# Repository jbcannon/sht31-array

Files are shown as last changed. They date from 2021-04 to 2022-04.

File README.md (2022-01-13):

# Overview

We have developed an open-platform temperature-humidity array for use in applications in forest and fire ecology. The following instructions provide step-by-step instructions for assembling the arrays and dataloggers. We also include software development and installation, and provide files to fabricate 3d-printed radiation shields, enclosures, and files necessary for manufacturing printed circuit boards for multiplexing.

 <p><p>Each section begins with materials required for assembly. Please read all instructions before begining to ensure all necessary materials are available. The material presented below details the construction of sensor and data loggers used in Cannon et al. (in prep). See manuscript for complete details on theory and applications.

* Complete assembly of [Particle Boron dataloggers](#data-logger-assembly-particle-boron-with-multiplexer) (1x)
* Fabricate [3d printed radiation shields](#3d-printed-radiation-shields) (8x shields)
* Fabricate [temperature and humidity sensor arrays](#SHT31-D-Sensor-arrays) (8x sensors)
* [Setting up Particle Boron-based dataloggers](#setup-and-test-boron-dataloggers)
  * Testing Particle Boron
  * Programing Particle Boron
  * Setting up cellular cloud data upload
 
<figure>
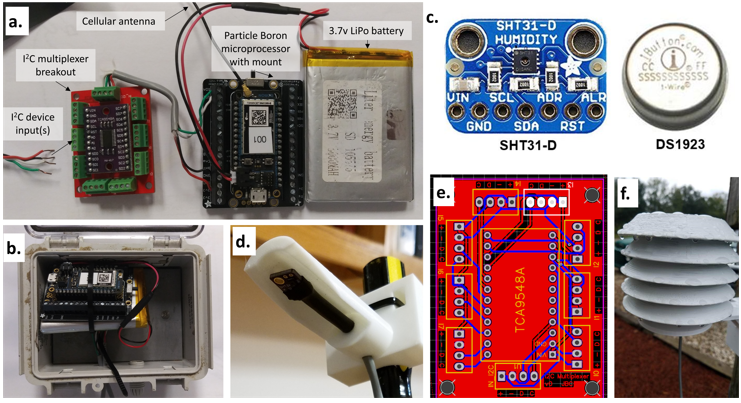
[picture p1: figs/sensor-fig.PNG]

<figcaption align = "center"><font size = -2>Figure 1. (a-f) Development of environmental monitoring using open-source platforms. (a) Datalogging assembly based on Particle Boron microprocessor on a screw terminal mount powered by a 3.7V 5000 mAH LiPo battery. Custom printed circuit board (PCB, red) includes I<sup>2</sup>C multiplexer chip allowing up to eight identically addressed sensors. (b) Datalogging assembly installed in weather resistant enclosure. (c) Comparison of Adafruit SHT31-D temperature and humidity sensor (left) and iButton Hygrochron (DS1932, right). (d) Minimalist radiation shield mount with installed SHT31-D sensor. (e) Custom PCB to use I<sup>2</sup>C multiplexer with 4-pin screw terminals. (f) 5-fin radiation shield 3D printed with PETG.<font></figcaption>
</figure>

 # Data logger Assembly (Particle Boron with multiplexer)
 
 Our system uses Particle Boron microcontrollers which have cellular network capabilities for remote data upload,  comprehensive documentation, and support numerous analog and digital devices using I<sup>2</sup>C or SPI. Our system uses multiple identically addressed SHT-31 sensors, which requires a multiplexer to allow reading of multiple sensors, thus we have created a custom printed circuit board that needs to be ordered or made.
 
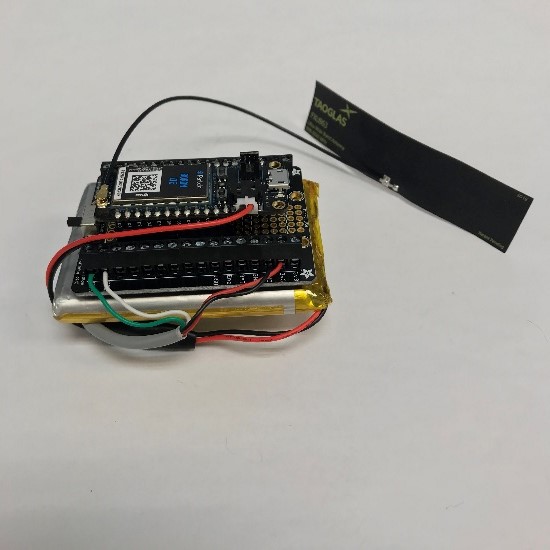
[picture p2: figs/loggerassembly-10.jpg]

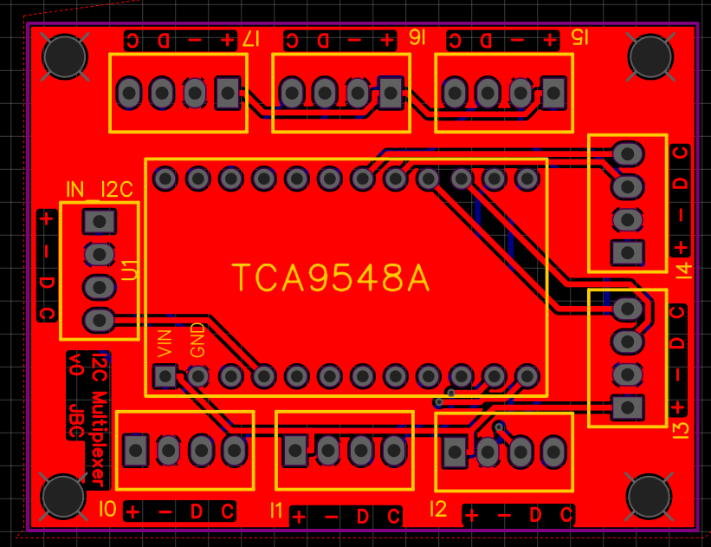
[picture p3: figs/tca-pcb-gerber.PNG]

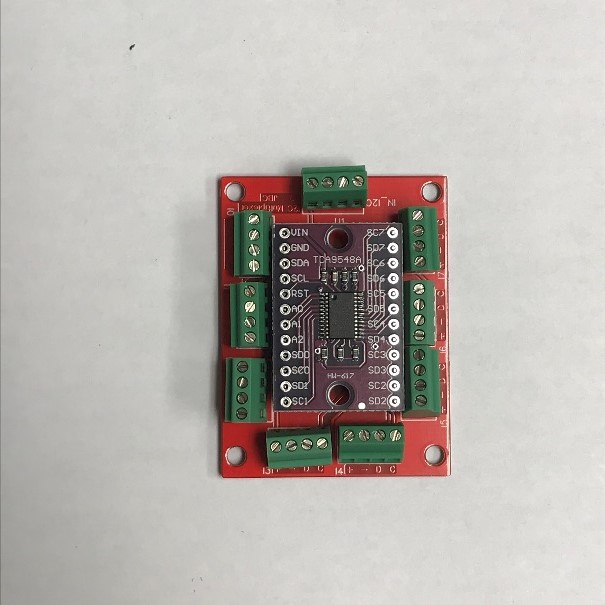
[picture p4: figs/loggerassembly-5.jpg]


 Follow the link to find complete instructions to <a href=pages/logger-assembly.md>assemble Particle Boron datalogger and multiplexer</a>

 # SHT31-D Sensor arrays

The SHT-31D sensor is an accurate temperature and humidity sensor with an accuracy of ±0.3°C and ±2% relative humidity. The sensor uses I<sup>2</sup>C connections and is therefore compatible with a wide variety of other I<sup>2</sup>C digital sensors, which allows for building more complex micro-meteorological stations.

 Follow the link to find complete instructions to <a href=pages/SHT-assembly.md>building SHT-31 sensor arrays</a>
 
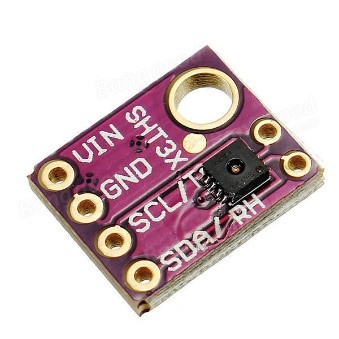
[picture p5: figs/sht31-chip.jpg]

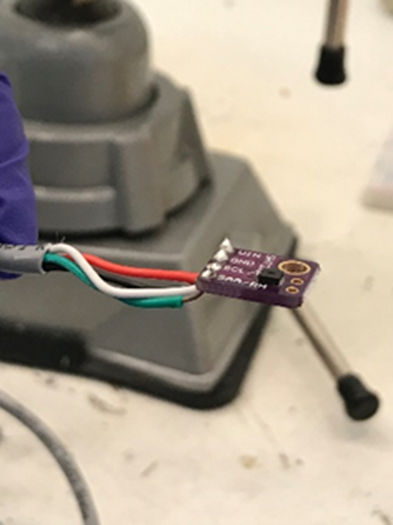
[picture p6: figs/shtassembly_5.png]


# 3D Printed radiation shields

To house the SHT31-D sensors, we provide plans and printing instructions for two radiation shield types, which include a minimalist radiation shield and a multi-fin radiation shield. 

Follow the link to find 3D models, photos, and printer settings for <a href=pages/3dprint.md>printing the radiation sheilds</a> on a PRUSA MK3 printer, or similar printer.

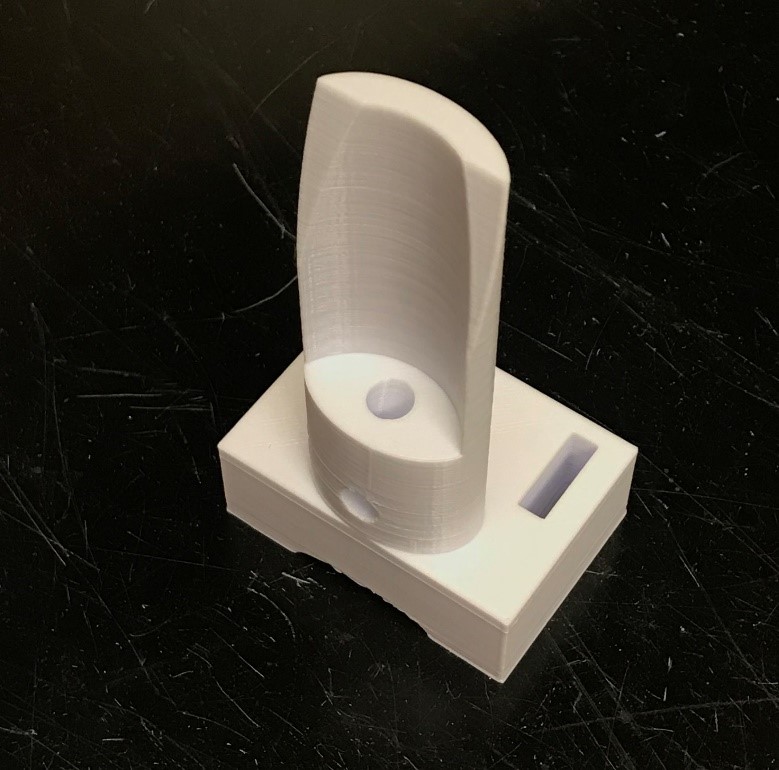
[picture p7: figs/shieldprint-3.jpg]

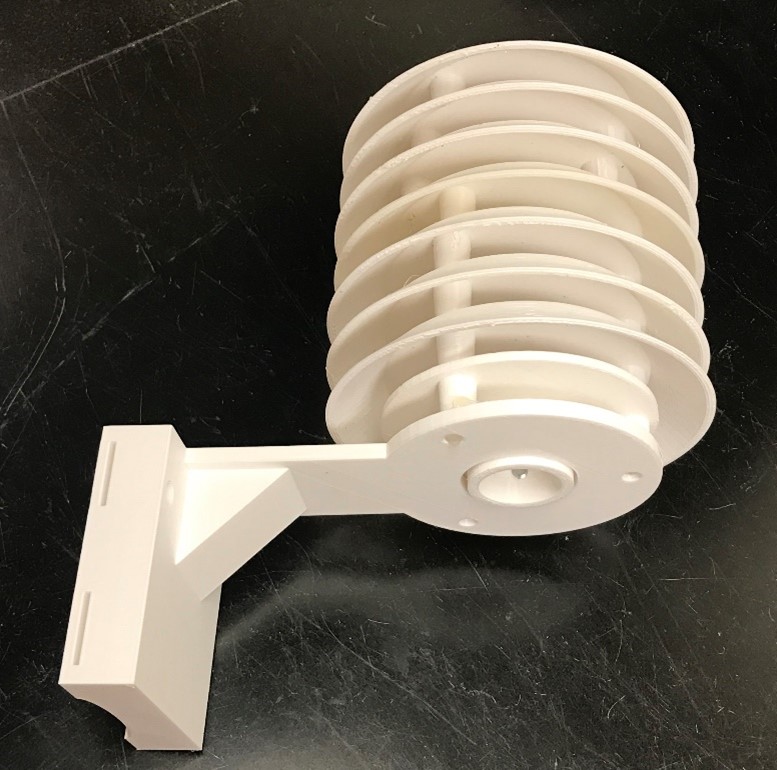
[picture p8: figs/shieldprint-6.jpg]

# Setup and test Boron dataloggers

Particle Boron offers a platform for interfacing with I<sup>2</sup>C sensors and connects to the web via cellular networks. 

Follow the link to find complete instructions to <a href=pages/boron-setup.md>activate and test Boron dataloggers<a/> with the SHT-31 sensors. The link includes instructions to activate through the Particle app for Android and iOS, testing upload apps and measurements, setting up cloud integration with Google Sheets, and deployment.

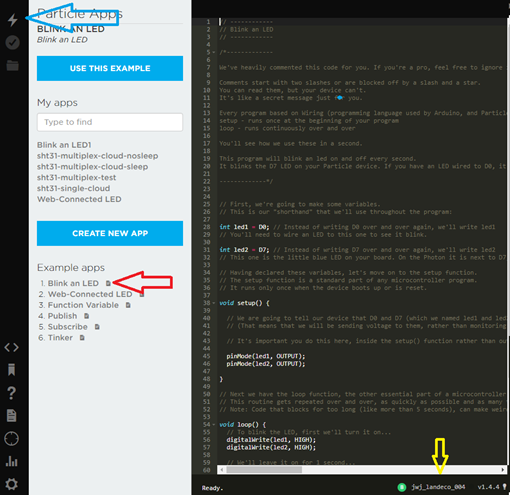
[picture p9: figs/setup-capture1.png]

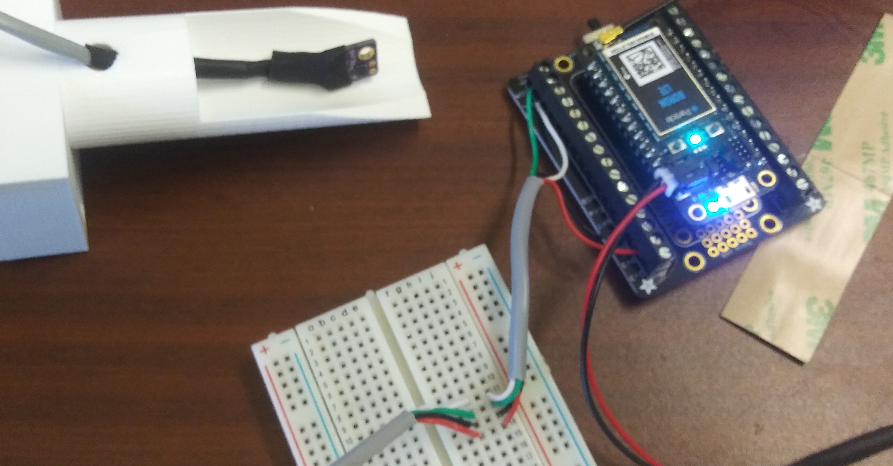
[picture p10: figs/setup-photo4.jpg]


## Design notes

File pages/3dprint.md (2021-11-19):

# SHT31-D 3D printed radiation shield

Our system uses a simple minimalist design for a 3d printed radiation shield. We provide plans and print settings for a minimalist radiation shield as well as a multi-fin radiation shield found on Thingiverse.  The following includes 3D model STL files used for housing SHT31-D sensors during field deployment, screenshots of two types of radiation shield models, 3D printer settings (for a Prusa I3 MK3S+ in PrusaSlicer software), and photographs of completed radiation shields.

## Tools & Materials
* PRUSA I3 MK3S+ 3D printer, or similar
* PrusaSlicer Software
* PETG filament, we recommend white
* Hot glue gun and glue cartridges or Cyanocoacrylate (CA) glue ("Super glue")

## Minimalist radiation shield

You can obtain a 3D model of the minimalist shield by downloading [minimalist-shield.stl](../files/minimalist-shield.stl).

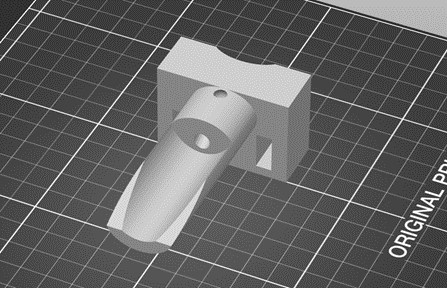
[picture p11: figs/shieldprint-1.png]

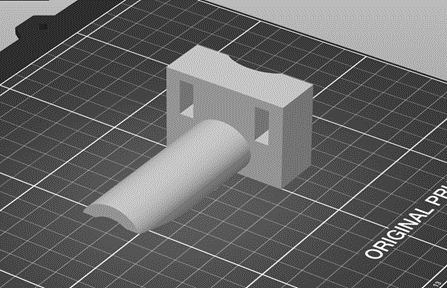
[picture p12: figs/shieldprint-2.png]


Using PRUSA Slicer, or similar software, we recommend the following print settings

| Printer setting | Recommended setting |
|----|---|
|Filament | Generic PETG |
| Nozzle temperature | 235°C |
| Bed temperature | 90°C |
| Layer Height | 0.2 mm (for all) |
| Infill | 25% |
| Support material | Check yes to "Generate support material" and yes to "Support on build plate only" |

Most of these settings are the default values for “0.20mm QUALITY @MK3” in PrusaSlicer software, with only the infill percentage increased and Nozzle/Bed temperatures adjusted to ensure the temperatures fall within range of the recommended temperatures for the brand/type of filament used.



## Multi-fin radiation shield

In the Cannon et al. XXXX study, we test radiation shields using a multi-fin design with 5 or 9 fins. You can obtain the 3D models for the components of the multi-fin shield by downloading the [multi-fin-shield](../files/multi-fin-shield/).

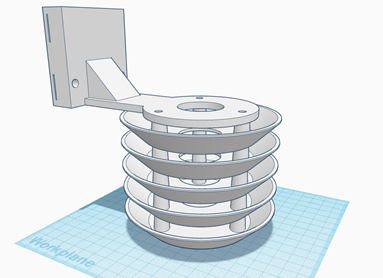
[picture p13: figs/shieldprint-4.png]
<br>
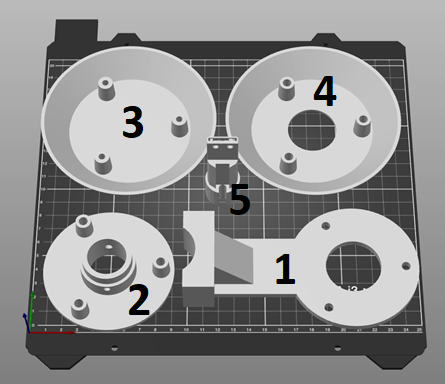
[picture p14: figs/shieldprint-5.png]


The [multi-fin-shield](../files/multi-fin-shield/) file contains the following \*.stl files:

1.  Radiation Shield Vertical Mount [Rad_Shd_Vert_mount_V1.stl](../files/multi-fin-shield/Rad_Shd_Vert_mount_V1.stl)
2.	Radiation Shield Base [Rad_Shd_Base_V1.stl](../files/multi-fin-shield/Rad_Shd_Base_V1.stl)
3.	Radiation Shield Top [Rad_Shd_Top_V1.stl](../files/multi-fin-shield/Rad_Shd_Top_V1.stl)
4.  Radiation Shield Fin [Rad_Shd_Fin_V1.stl](../files/multi-fin-shield/Rad_Shd_Fin_V1.stl)
5.	SHT31/iButton Sensor Holder [SHT31_iButton_plugV2.stl](../files/multi-fin-shield/STH31_iButton_plugV2.stl)

Use the same settings as the minimalist shield. Some parts such as the Sensor Holder will need support, and others such as the Fins, Base, and Top, will not.

You can print multiple copies of the Radiation Shield Fin to make any sized radiation shield

Once printed, all parts can be stacked and glued together (superglue or hot glue).



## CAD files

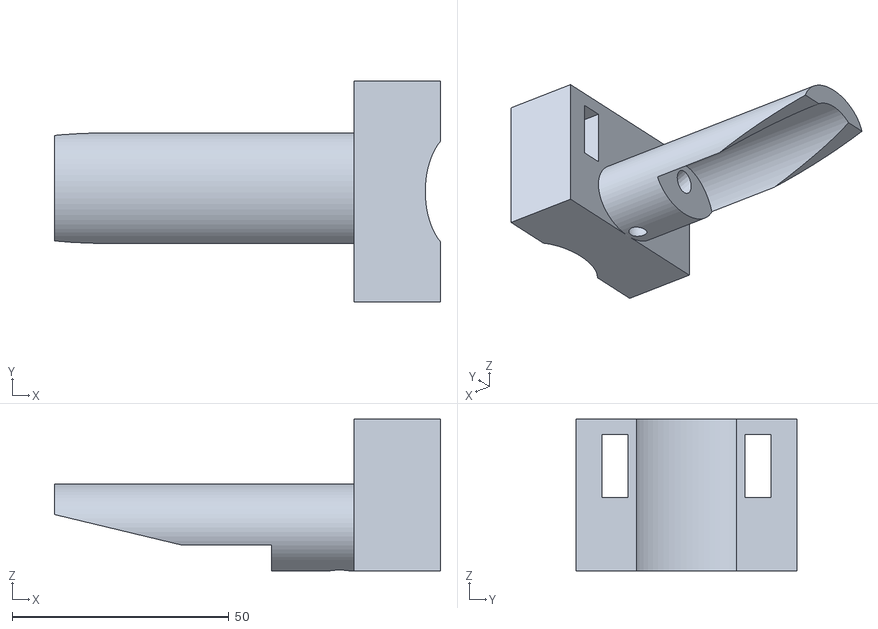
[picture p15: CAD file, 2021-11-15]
files/minimalist-shield.stl
89.0 x 51.0 x 35.0

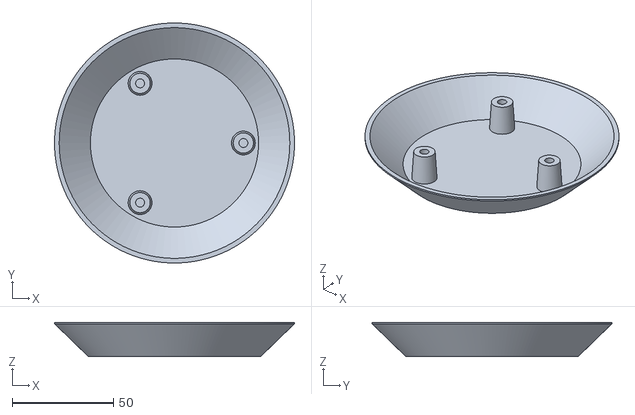
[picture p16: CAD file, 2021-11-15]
files/multi-fin-shield/Rad_Shd_Top_V1.stl
118.5 x 118.5 x 17.0

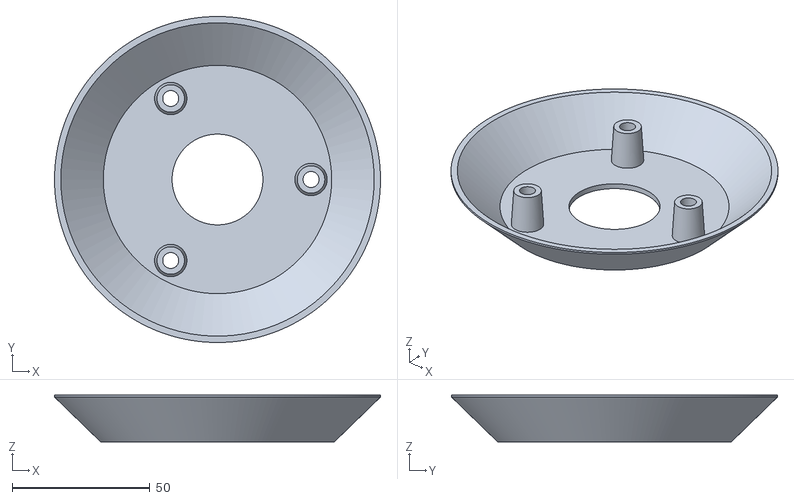
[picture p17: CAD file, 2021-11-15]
files/multi-fin-shield/Rad_Shd_Fin_V1.stl
118.5 x 118.5 x 17.0

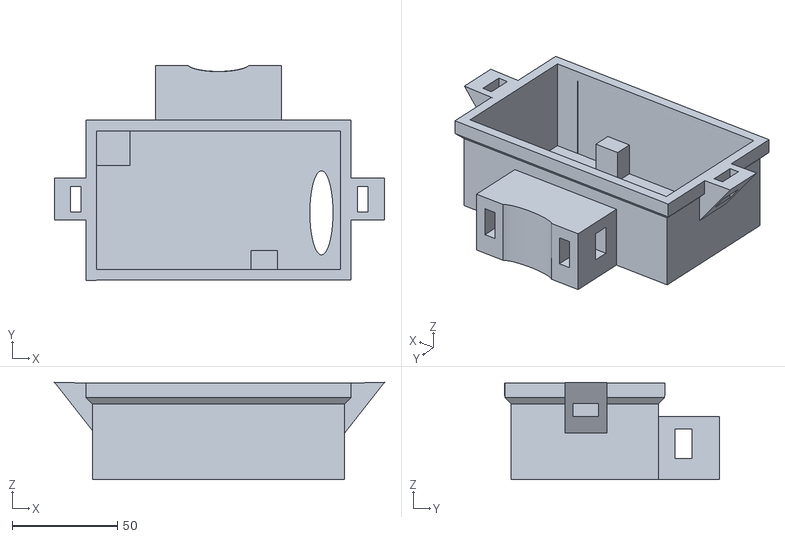
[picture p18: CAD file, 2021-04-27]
files/Zip_Tie_Box.stl
157.0 x 102.1 x 46.3

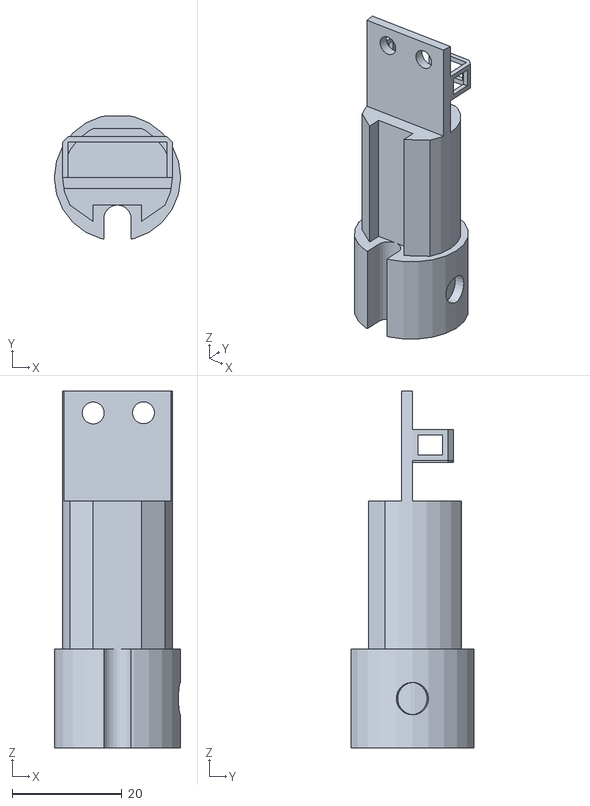
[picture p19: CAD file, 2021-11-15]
files/multi-fin-shield/STH31_iButton_plugV2.stl
23.0 x 22.4 x 65.0

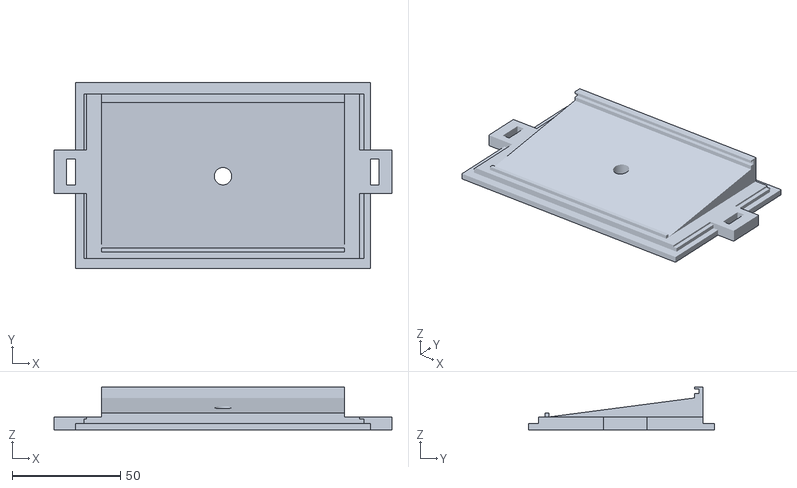
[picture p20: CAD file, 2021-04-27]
files/Zip_Tie_Lid.stl
155.8 x 85.8 x 19.8

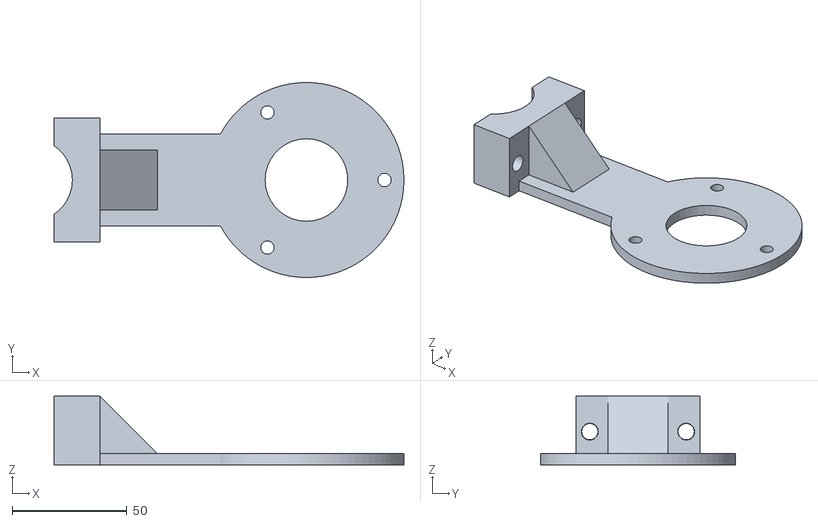
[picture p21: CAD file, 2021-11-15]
files/multi-fin-shield/Rad_Shd_Vert_mount_V1.stl
152.5 x 85.0 x 30.0

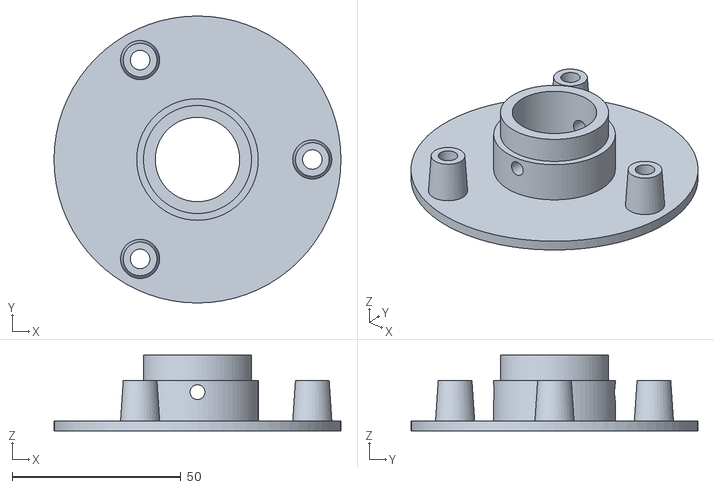
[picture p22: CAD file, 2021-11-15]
files/multi-fin-shield/Rad_Shd_Base_V1.stl
85.0 x 85.0 x 22.5

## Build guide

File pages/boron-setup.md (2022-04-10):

# Activation

Activating Particle Boron is simple and Particle has good documentation to aid with the activation. 

You will need
* Assembled datalogger from [previous step](logger-assembly.md)
* Bluetooth enabled Android or iOS device installed with Particle app downloaded from [Google Play](https://play.google.com/store/apps/details?id=io.particle.android.app&hl=en_US&gl=US) or [Apple Store](https://apps.apple.com/us/app/particle-iot/id991459054)
* One or more SHT31 sensor assemblies [from previous step](SHT-assembly.md)

With the battery from the assembled logger plugged in, follow the steps below to activate. [Steps to Activate Particle Boron](https://www.youtube.com/watch?v=xymSayKBGbg). Because your logger is powered by a battery, you do not need the USB connector. After following the steps in the video, you should have an activated device, and have updated firmware to the device which is automatically uploaded via the cellular connection.

Click image to watch video 



# Testing

## Uploading Blink Sketch

* Once your Particle Boron is activated, it is best to complete a few tests to ensure your device is working properly.
* Log in to the [Particle Web IDE](https://build.particle.io/build)



- Under Example apps, select the Blink an LED sketch from the list (Red arrow)
- Check that the name of the device you just setup matches what is indicated by the yellow arrow. If not, click the name and indicate the correct device from the Particle Device list
- Once the correct device is selected, click the Flash button (blue arrow). This will upload the sketch to the Boron. 
- As the sketch is uploading, you should see a series of flashes. See here for a guide to [Particle Boron LED status indicators](https://docs.particle.io/tutorials/device-os/led/boron/)
  - Slow blinking green means the device is searching for signal.
  - Slow blinking cyan means Signal is found.
  - Fast blinking cyan means data transfer is occurring.
  - Magenta light appears when the app is flashed onto the device.
- Once the sketch is successfully updated, you should see a blue blink from the LED located next to the USB connector on the Boron.

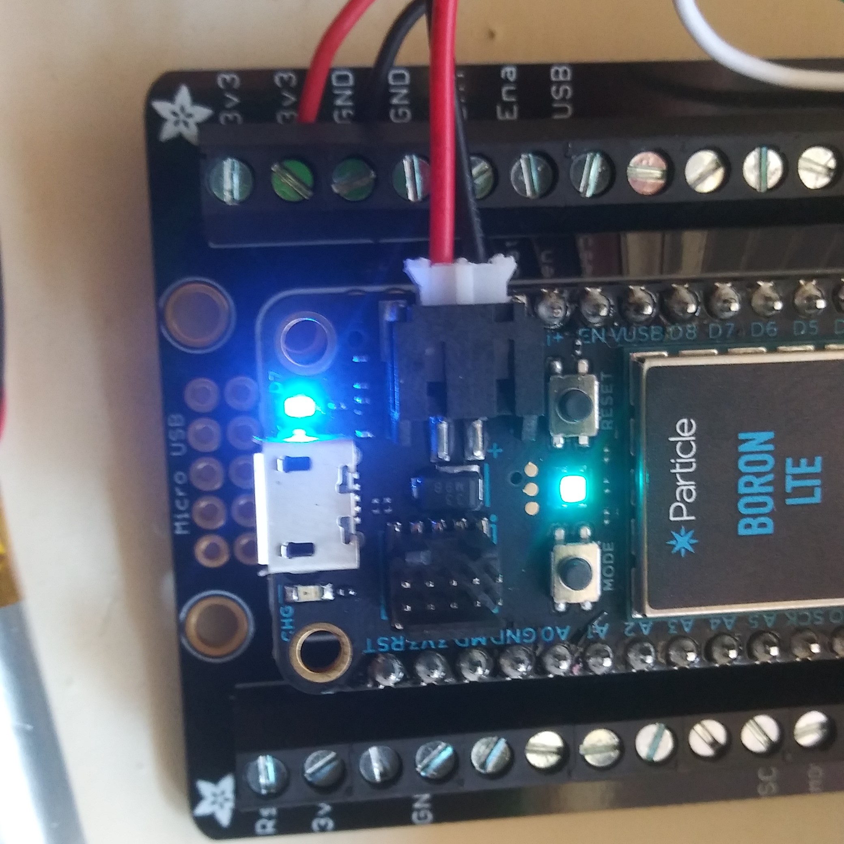
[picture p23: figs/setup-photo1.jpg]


## Testing SHT31 sensor

-	After successfully uploading the Blink sketch, connect a single SHT-31 sensor and upload a sketch that will upload the readings to Particles Cloud platform.
-	Release the 4 wires connected to the I<sup>2</sup>C multiplexer PCB assembly, and place each wire into a bread board as shown below. This will allow rapid connection of several single I<sup>2</sup>C devices to the Boron for testing and troubleshooting.
-	Connect one of the assembled SHT31 sensors to the corresponding cables. If you followed our construction, the pin associations are

| Wire | Pin |
| -- | -- |
| Red	| VCC |
| Black	| GND |
| Green	| SDA |
| White	| SCL |

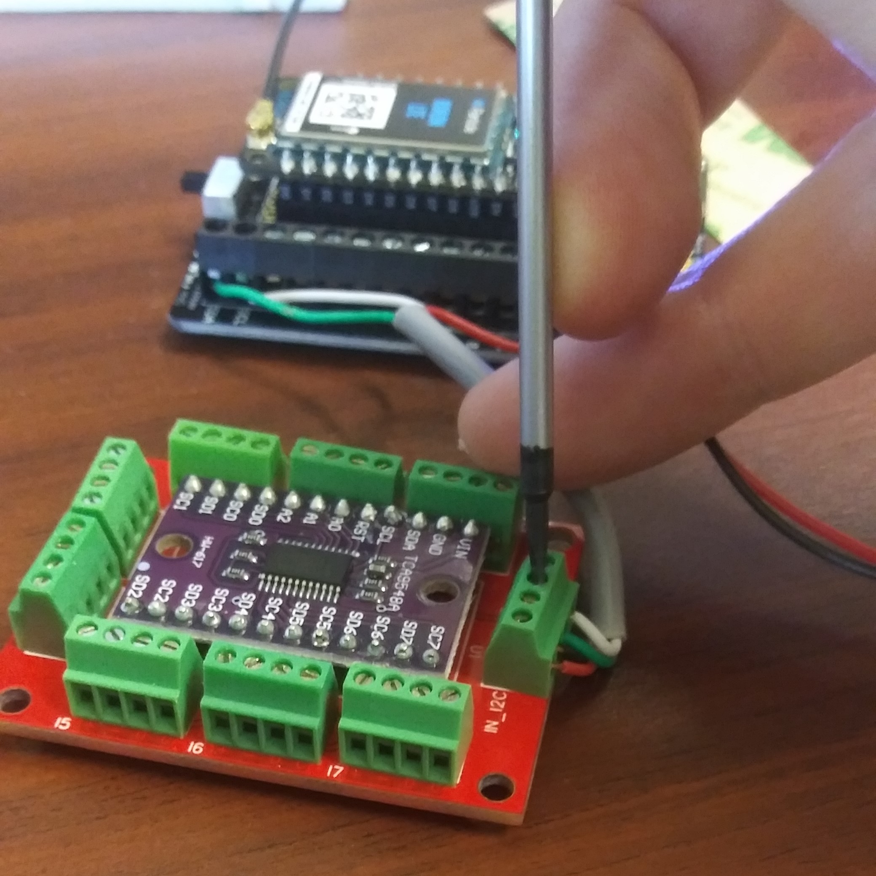
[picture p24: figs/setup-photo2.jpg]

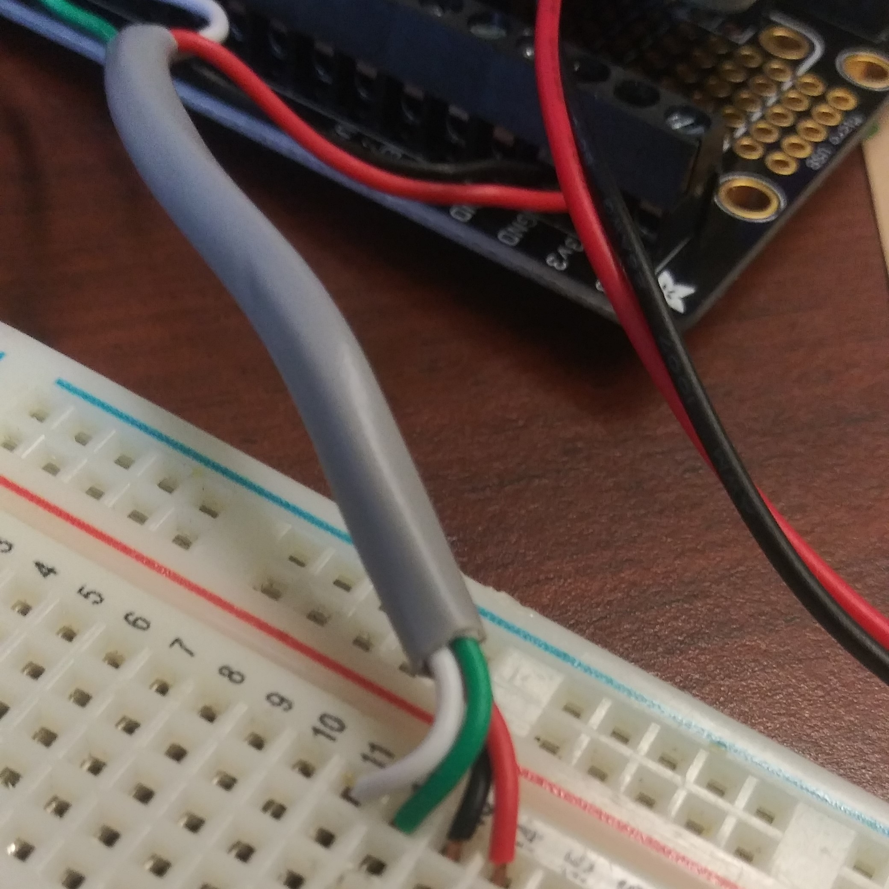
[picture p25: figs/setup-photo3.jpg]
<br>


-	In the Particle Web IDE, select the Code Symbol (< >) on the left hand side, and select Create New App
-	Name the app `sht31-single` or similar
-	Select the Libraries button from the lefthand side (bookmark) and search `adafruit-sht31`. Select the library, and click the “Include in Project” button. Select the app you just named and confirm its inclusion.
-	The following code reads the temperature and humidity of the logger and publishes it to Particles Console for viewing. Paste the following code into the code window and select the Flash button to upload the app.

```
// This app reads a single an SHT-31 sensor connected via I2C and uploads to Particle Console
#include <adafruit-sht31.h>
Adafruit_SHT31 sht31 = Adafruit_SHT31();

void setup() {
    Wire.begin();
    sht31.begin(0x44);
    delay(1000);
}

void loop() {
    if(Time.second() == 0){
      float t = sht31.readTemperature();
      float h = sht31.readHumidity();
      Particle.publish("temperature", String(t));
      Particle.publish("humidity", String(h));
      char payload[128] = "";
      sprintf(payload,"{\"temp\":%.2f,\"hum\":%.2f}", t, h);
      delay(1000);
    }
}
```

- You will know the flash is successful when the cyan LED returns to blinking *breathe* mode. Click on the Console icon. You will see an Events table listing all status updates related to your Particle devices. The app you created reads and uploads the temperature and humidity once per second.
- Verify that humidity and temperature readings are valid. If you are not getting readings, check all wired connections with the sensor.
- In areas with a slow cellular connection, updates may occur at greater than 1 second intervals.
- Remove the SHT31-sensor form the breadboard and repeat seven times, connecting each additional sensor on the breadboard in turn until all sensors are tested.
 
# I<sup>2</sup>C and cloud upload
- The Particle console offers a convenient way to communicate directly with the datalogger, but does not serve for convenient data storage. To setup data logging from Particle Boron to Google Sheets, you will need to use the following steps.
- Follow the steps to [setup integration of Particle and Google Sheets](https://github.com/deancs/particlePostGoogle). This script guides you through the process to setup an empty GoogleSheet to contain data, integrate a script using the Script Editor, create and use a Particle security token, and link your script with a Particle Webhook
•	Create a new app in the Particle Web IDE and paste the following code and Flash the following script to your device. This code takes measurements at an `interval` of 5 seconds and uploads data continuously to the Cloud. Note that this requires a continuous cellular network connection that may deplete battery life in ~10 days. See below for code to decrease upload rates and extend battery life. 

```
#include <adafruit-sht31.h>
#include <TCA9534.h>

const int interval = 5; // reading interval (in seconds), should be a divisor of 60 (e.g., 1, 2, 5, 6, 12, 15, 30)

// Instantiate Temperature - Humidity Sensor(s)
#define TCAADDR 0x70 // Address of TCA9548A I2C Multiplexer
Adafruit_SHT31 sht31 = Adafruit_SHT31();
FuelGauge fuel;

char payload[128] = "";

void setup() {
    Wire.begin();
}

void loop() {
    if(Time.second() % interval == 0){
        float t [8];
        float h [8];
        for (uint8_t bus=0; bus<8; bus++) {
          t[bus] = readTemp(bus, 0x44);
          h[bus] = readHumid(bus, 0x44);
          if(isnan(t[bus])) t[bus] = -100;
          if(isnan(h[bus])) h[bus] = -100;
        }
        float soc = fuel.getNormalizedSoC();
        float vbatt = fuel.getVCell();
        sprintf(payload,"{\"charge\":%.1f,\"Vbatt\":%.2f,\"temp0\":%.1f,\"hum0\":%.1f,\"temp1\":%.1f,\"hum1\":%.1f,\"temp2\":%.1f,\"hum2\":%.1f,\"temp3\":%.1f,\"hum3\":%.1f,\"temp4\":%.1f,\"hum4\":%.1f,\"temp5\":%.1f,\"hum5\":%.1f,\"temp6\":%.1f,\"hum6\":%.1f,\"temp7\":%.1f,\"hum7\":%.1f}", soc, vbatt, t[0], h[0], t[1], h[1], t[2], h[2], t[3], h[3], t[4], h[4], t[5], h[5], t[6], h[6], t[7], h[7]);
        Particle.publish("postGoogle", payload); //post to GoogleSheets
        delay(1s);
    }
}

// Function to read temperature from select TCA and address (bus = 0-7, addr = 0x44 or 0x45)
float readTemp(int bus, int addr) {
    Wire.beginTransmission(TCAADDR);
    Wire.write(1 << bus);
    Wire.endTransmission();
    sht31.begin(addr);
    delay(500);
    float temp = sht31.readTemperature();
    return(temp);    
}

// Function to read humidity from select TCA and address (bus = 0-7, addr = 0x44 or 0x45)
float readHumid(int bus, int addr) {
    Wire.beginTransmission(TCAADDR);
    Wire.write(1 << bus);
    Wire.endTransmission();
    sht31.begin(addr);
    float humid = sht31.readHumidity();
    return(humid);    
}
```

* This code utilizes the `Particle.sleep()` function and local (RAM) data storage to increase battery life up to an estimated 180 days.
* The function takes a reading ever `INTERVAL` (in minutes) and stores data locally. Once the total number of records colelcted reaches `RECORDS_PER_UPLOAD` the data is uploaded to the Cloud.
* Note that < 80 kB of RAM data storage is available on Particle Boron, thus use caution if using `RECORDS_PER_UPLOAD` > 60 as RAM capacity may be exceeded.

```
#include <adafruit-sht31.h>
#include <TCA9534.h>

#define INTERVAL 15 // reading interval (in minutes), should be a divisor of 60 (e.g., 1, 2, 5, 6, 12, 15, 30)
#define RECORDS_PER_UPLOAD 12 // how many readings to take before uploading
char payload[RECORDS_PER_UPLOAD][1024] = {"","","","","","","","","","","",""};  // Put a set of apostrophes equal to the number of RECORDS_PER_UPLOAD.
#define TIMEZONE -4

// Instantiate Temperature - Humidity Sensor(s)
#define TCAADDR 0x70 // Address of TCA9548A I2C Multiplexer
#define PUBLICATION_DELAY 4000 // delay between Particle.publish() events (in ms) to prevent readings out of order.
Adafruit_SHT31 sht31 = Adafruit_SHT31();
FuelGauge fuel;
SystemSleepConfiguration config;
SYSTEM_MODE(SEMI_AUTOMATIC);

int record = 0;

void setup() {
    /// Connect to cloud and sync time.
    Particle.connect();
    waitUntil(Particle.connected);
    Particle.syncTime();
    waitUntil(Particle.syncTimeDone);
    delay(5s);
    Particle.disconnect(CloudDisconnectOptions().graceful(true).timeout(30s));
    Time.zone(TIMEZONE); 

    Wire.begin();
    RGB.control(true);
    for(int i=0; i<4; i++) { // flash color to indicate successful connection
        RGB.control(true);
        RGB.color(255,255,255);
        delay(200);
        RGB.color(10,0,0);
        delay(200);
        RGB.color(0,0,0);
    }
}

void loop() {
    if(Time.minute() % INTERVAL == 0 & Time.second() == 0){
        String current_time = Time.format(Time.now(), "%F %T");
        //String current_time = Time.timeStr();
        float t [8];
        float h [8];
        for (uint8_t bus=0; bus<8; bus++) {
          RGB.control(true);
          RGB.color(255,0,0);
          t[bus] = readTemp(bus, 0x44);
          h[bus] = readHumid(bus, 0x44);
          if(isnan(t[bus])) t[bus] = -100;
          if(isnan(h[bus])) h[bus] = -100;
          delay(200);
          RGB.color(0,0,0);
          delay(200);
        }
        float soc = fuel.getNormalizedSoC();
        float vbatt = fuel.getVCell();
        sprintf(payload[record],"{\"time\":\"%s\",\"record\":%d,\"charge\":%.1f,\"Vbatt\":%.2f,\"temp0\":%.1f,\"hum0\":%.1f,\"temp1\":%.1f,\"hum1\":%.1f,\"temp2\":%.1f,\"hum2\":%.1f,\"temp3\":%.1f,\"hum3\":%.1f,\"temp4\":%.1f,\"hum4\":%.1f,\"temp5\":%.1f,\"hum5\":%.1f,\"temp6\":%.1f,\"hum6\":%.1f,\"temp7\":%.1f,\"hum7\":%.1f}",
            current_time.c_str(), record, soc, vbatt, t[0], h[0], t[1], h[1], t[2], h[2], t[3], h[3], t[4], h[4], t[5], h[5], t[6], h[6], t[7], h[7]);
        Serial.print("Record "); Serial.println(record);
        Serial.println(payload[record]);
        Serial.println("=========");
        record = record + 1;        
        
        /// Once the appropriate number of records has been collected, upload them and dump data.
        if(record == RECORDS_PER_UPLOAD) {
            // reconnect to particle cloud
            Serial.println("Connecting to the cloud");
            if (!Particle.connected()) {
                    Particle.connect();
                    waitUntil(Particle.connected);
                    if(Particle.connected()) Serial.println("Succesfully connected"); else Serial.println("Connection unsucessful");
                    Particle.syncTime();
                    waitUntil(Particle.syncTimeDone);
            }
            
            Serial.println("Preparing to upload all records");
            // upload all records
            for(int i = 0; i < RECORDS_PER_UPLOAD; i++) {
                Serial.print("Uploading record: ");
                Serial.println(i);
                Serial.print(payload[i]);
                Serial.println("================");
                bool success = try_to_publish(payload[i], 3); //post to GoogleSheets
            }
            record = 0;
            Serial.println("Records uploaded to the cloud");
            Serial.println("Discconecting");
            Particle.disconnect(CloudDisconnectOptions().graceful(true).timeout(30s));
            Serial.println("Discconected");
        }
        
        Serial.println("Going to sleep");
        /// go to sleep after measurement
        config.mode(SystemSleepMode::STOP)
            .duration(INTERVAL * 1000 * 60 - 30000) // sleep for 30 seconds shorter than interval
            .flag(SystemSleepFlag::WAIT_CLOUD); // complete any cloud api activities before sleeping
        System.sleep(config);
        Serial.println("Waking up");
    }
}

// Function to read temperature from select TCA and address (bus = 0-7, addr = 0x44 or 0x45)
float readTemp(int bus, int addr) {
    Wire.beginTransmission(TCAADDR);
    Wire.write(1 << bus);
    Wire.endTransmission();
    if(!sht31.begin(addr)) return(-100); else {
        float temp = sht31.readTemperature();
        return(temp);    
        }
}

// Function to read humidity from select TCA and address (bus = 0-7, addr = 0x44 or 0x45)
float readHumid(int bus, int addr) {
    Wire.beginTransmission(TCAADDR);
    Wire.write(1 << bus);
    Wire.endTransmission();
    if(!sht31.begin(addr)) return(-100); else {
        float humid = sht31.readHumidity();
        return(humid);  
    }
}

bool try_to_publish(char payload[1024], int tries) {
    bool success = false;
    for(int i = 0; i < tries; i++) {
        if(success == false) {
            success = Particle.publish("postGoogle", payload);
            delay(PUBLICATION_DELAY);
        }
    }
    return(success);
}
```

# Deployment
- Reconnect the I<sup>2</sup>C multiplexer assembly to the Screw terminal block 
- Connect up to eight SHT31 sensors to the screw terminals on the SHT31 assembly. Depending on the enclosure you wish to use, you may need to feed the lines through a valve in the enclosure before screwing them down.
- Use a zip-tie to bundle the Particle Boron, Multiplexer Assembly, and battery into one unit, and place in the enclosure.
- Once turned on and connected, the device will upload 8 readings to the setup Google Sheets using the webhook and Google Script integration. Each device you use will create its own tab in the Google worksheet



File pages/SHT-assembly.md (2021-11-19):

# SHT31-D temperature and Humidity array assembly protocol

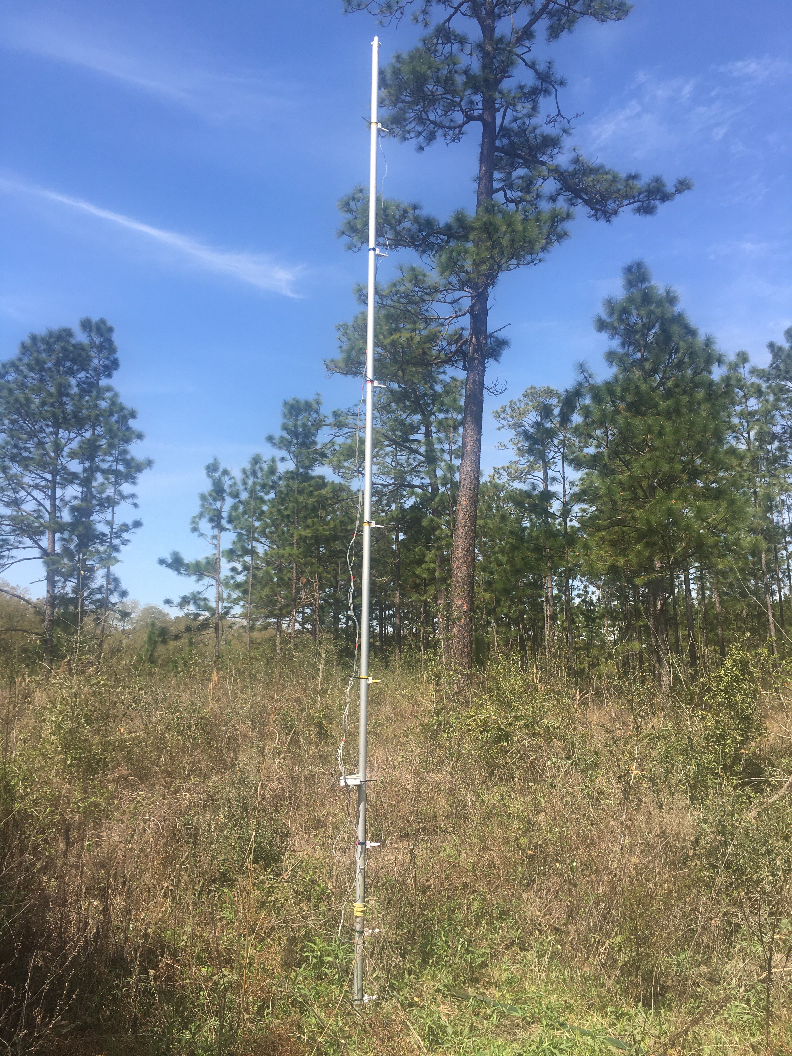
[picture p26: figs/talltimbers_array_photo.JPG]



## Tools
-	Soldering iron and lead-free solder
-	Brass Sponge to prolong soldering tip life
-	Wire strippers
-	Flush cutting pliers or other cutting tool
-	Bench-top clamp (not essential but greatly simplifies the process)
-	heat gun, blow dryer, or lighter for heat shrink

## Materials
-	SHT31-D breakout board (e.g., from [Adafruit](https://www.adafruit.com/product/2857), [Aliexpress](https://www.aliexpress.com/item/32850554676.html) or [Amazon](https://www.amazon.com/Temperature-SHT31-D-Humidity-Breakout-Weather/dp/B073P6G2Q4/))
-	Shielded cable, 4 wire, solid core 22 AWG (lengths will vary)
-	Heat shrink tubing (1/4" and 1/2" diameter ([Amazon](https://www.amazon.com/gp/product/B01KYFZRQW))
-	JST or other 4-pin connectors (if your datalogger requires it). The Particle Boron-based dataloggers we recommend do not require connectors. [Amazon](https://www.amazon.com/Connector-Include-Ph2-0-Female-Ph2-0mm/dp/B08RHGT3W3/)

## Assembly

- Cut a piece of 22 AWG 4-wire cable to the desired length. For our 8 sensor array, we mounted a data logger at 1.5 m. For this height, cut lenghts according to the following table

Height | Cable length
-- | --
6 m | ~5 m
5 m | ~4 m
4 m | ~3 m
3 m | ~2 m
2 m | ~0.75-1 m
1 m | ~0.75-1 m
0.5 m | ~1.5 m
0 m | ~2 m

- Prep each end of the cable by stripping ~3 cm of the main shielding away from the four wires inside, and then ~1 cm of shielding away from each of the wires.

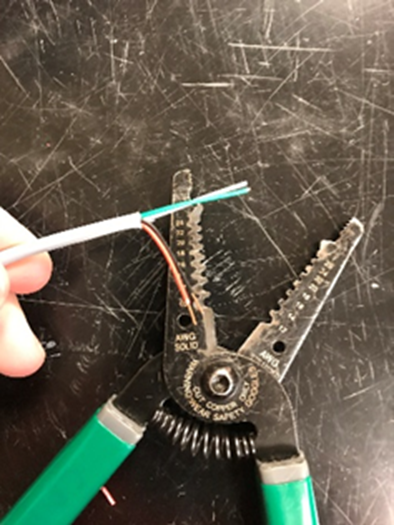
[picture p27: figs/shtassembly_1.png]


- Place the SHT31 sensor in the clamp or on a surface where the wires are easily fed through each pinhole on the board. Solder each wire individually in its respective place (suggested placements are indicated below). Good solder joints should resemble a bell-shape or Hershey’s kiss rather than a sphere-shape which indicates additional flux may be needed. See here for [tips on soldering breakout boards](http://www.youtube.com/watch?v=3230nCz3XQA&t=3m40s).

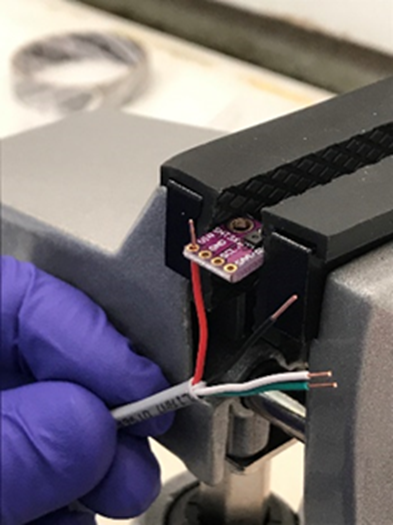
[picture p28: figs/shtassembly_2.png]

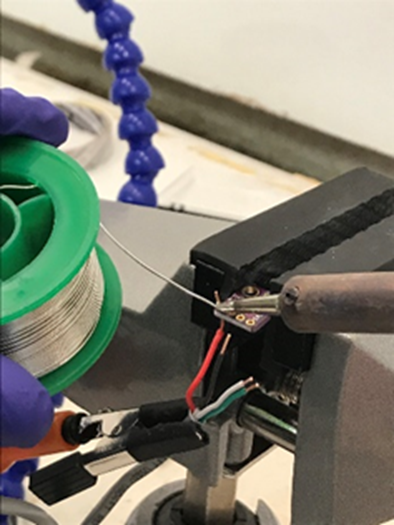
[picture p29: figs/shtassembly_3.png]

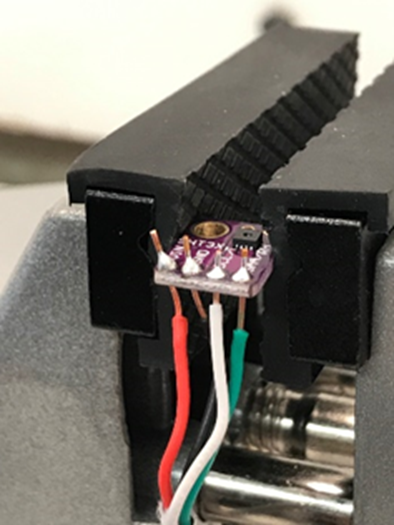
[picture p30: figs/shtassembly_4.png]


Pin | Cable
-- | --
VIN | Red
GND | Black
SCL | White
SDA/SAA | Green

-	Trim the excess length from each wire to the top of the solder and straighten wire out so that the sensor and cable are in line. Test the sensor using an assembled tester and Arduino software to ensure all connections are correctly made.


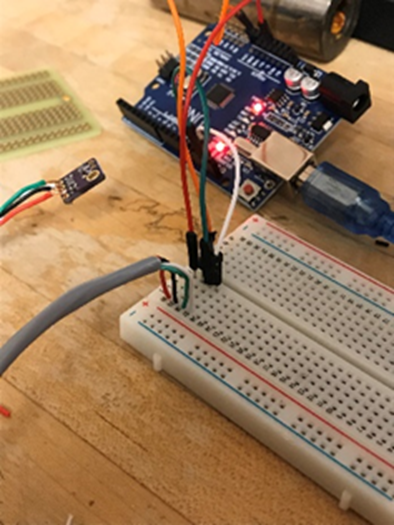
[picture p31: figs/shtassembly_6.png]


-	Cut a piece of 1/4" diameter heat shrink long enough to cover the exposed wires of the sensor (no longer than 4 cm to ensure that the sensor can correctly slide into housing) and place on the cable. Use the heat gun/blow dryer to seal it in place. Then, cut a short piece (approximately 2 cm) of 1/2" diameter heat shrink and place over the soldered pins and most of the sensor. Do not cover the black square chip on the sensor with heat shrink. 
	
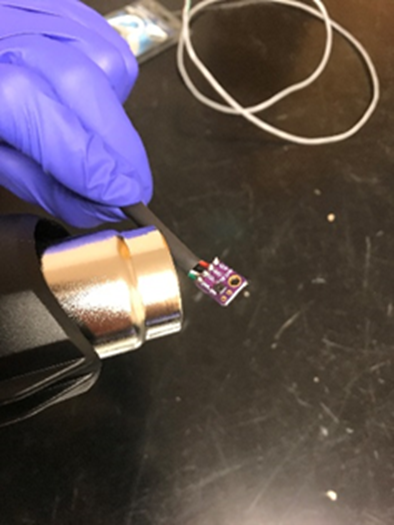
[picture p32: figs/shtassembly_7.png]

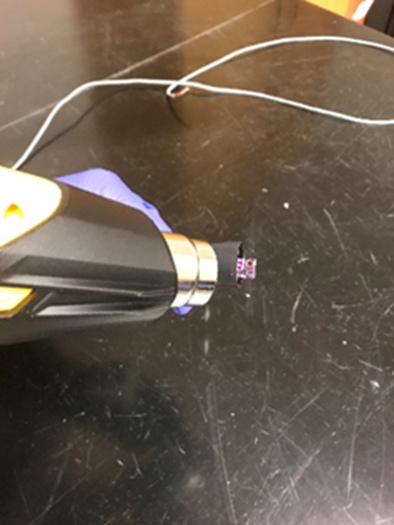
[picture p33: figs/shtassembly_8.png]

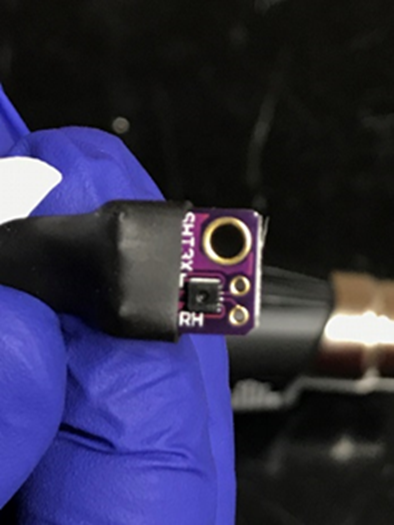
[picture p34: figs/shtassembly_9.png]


** NEED TO ADD LINK to MOUNT **

-Feed the bare end of the cable through the channel into the [3d printed sensor mount](#).

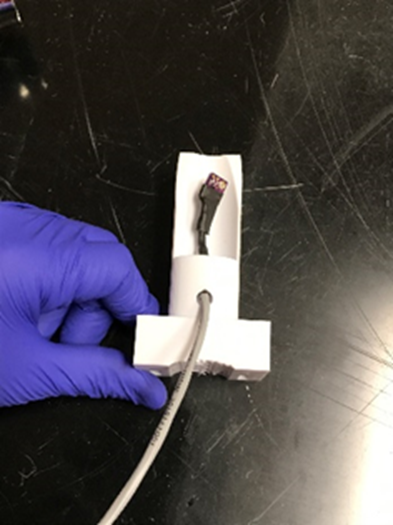
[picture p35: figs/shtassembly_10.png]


- Repeat the above steps until you have 8 sensor assemblies.
- **If your data logger uses screw terminals** (e.g., the Particle Boron-based datalogger which we recommend) then assembly of a single unit is complete. 
- If if you would like to add a JST 4-pin plug or another connector for some devices, continue on to the additional steps. However, in our experience the JST plugs are brittle and thus somewhat finicky

<hr>

- **If your datalogger requires a JST or other plug**, Slide a 3" piece of 1/4" diameter heat shrink on the cable before attaching a plug. Once the plug is installed you will no longer be able to add the heat shrink.
- Cut the wires of the plug down to ~2 cm long and strip ~0.5 cm away from the end (these wires are stranded and need to be twisted at the ends in order to keep internal wires together). Tin the ends of each wire on both the plug and the cable. (Figure 11-13)

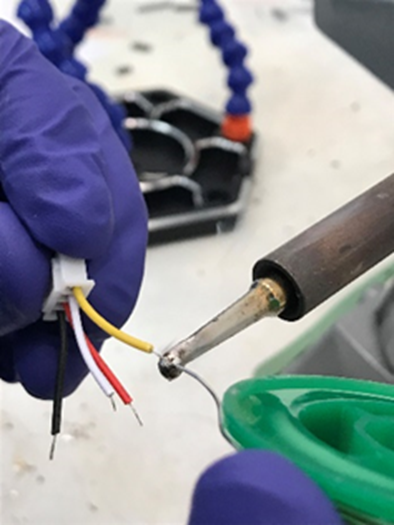
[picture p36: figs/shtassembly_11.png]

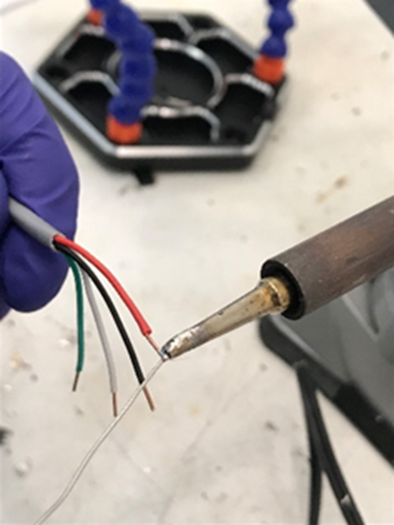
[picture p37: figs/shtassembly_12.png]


-Ensure the wires are lined up in the appropriate order as shown in the wiring table below. Then apply solder to the end of the soldering iron (held in the clamp if possible), take a wire in each hand, and simultaneously place them in the solder on the iron tip. Once they have enough solder on them, lift them out together and allow the solder to cool to complete the connection. This process can be repeated until a strong, even connection is made between the two. 

Plug | Cable | Sensor
-- | -- | --
Black | Red | VIN
Red | Black | GND
White | White | SCL
Yellow | Green |SDA/SAA

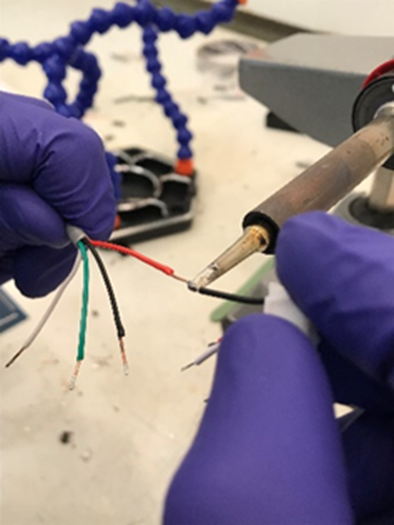
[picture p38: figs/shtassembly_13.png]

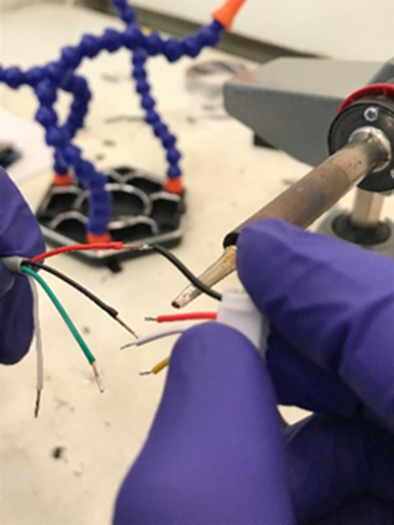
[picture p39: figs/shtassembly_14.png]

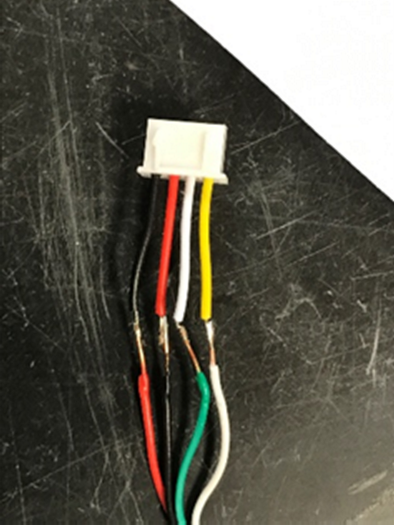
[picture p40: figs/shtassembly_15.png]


- Cut small pieces of electrical tape and wrap them around each exposed connection between the cable and the plug. Trim any excess and then slide heat shrink down over the bare wires and use the heat gun/blow dryer to seal it.

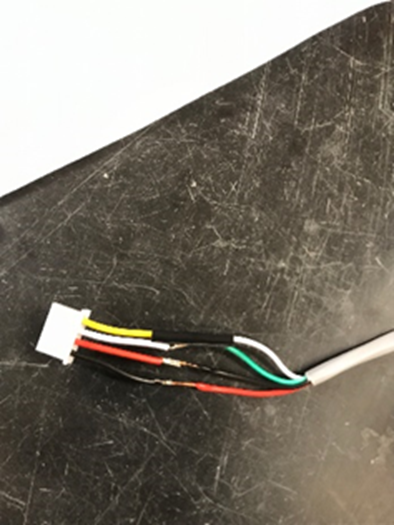
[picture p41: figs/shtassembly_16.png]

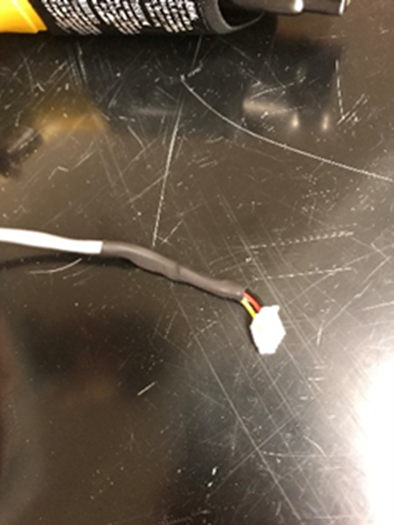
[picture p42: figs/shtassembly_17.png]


- Label the back of the sensor mount with the appropriate mounting height (depends on the length of the cable). Refer to the “Sensor Height” table.

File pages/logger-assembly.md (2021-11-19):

# Particle Boron datalogger assembly

The Particle Boron is a development kit that supports cellular network. This guide illustrates tools, materials, and instruction for connecting the Particle Boron to a Multiplexer to allow up to 8 identically addressed I<sup>2</sup>C busses. 
 
 **Please note that if you only need one or two SHT-31 sensors attached to a data logger, the multiplexer is unnecessary. Simply attach the Boron to the Terminal block, and insert a battery**. The remaining steps involving the multiplexer are unnecessary and can be skipped.

## Tools
- Soldering iron and lead-free solder
- Wire strippers

## Materials

-	Particle Boron Kit (LTE CAT-M1) (NorAm) ([Particle](https://store.particle.io/collections/ethersim/products/boron-lte-cat-m1-noram-ethersim))
-	Adafruit Terminal Block Breakout FeatherWing ([Adafruit](https://www.adafruit.com/product/2926))
-	3.7V Lithium Battery with 2-pin female plug ([AliExpress](https://www.aliexpress.com/item/32846169676.html))
 
 If you would like to link the datalogger to more than two SHT-31 sensors, or have identically addressed I<sup>2</sup>, you will also need the following materials to allow multiplexing capabilities. 
 
- TCA9548A Multiplexer Module ([Adafruit](https://www.adafruit.com/product/2717) | [AliExpress](https://www.aliexpress.com/wholesale?SearchText=TCA9548A))
-	TCA9548A PCB Board ([contact me](mailto:jeffery.cannon@jonesctr.org) for a few, or see below for ordering a custom PCB)
-	5-6” length of 22AWG 4-wire solid core cable
-	9 4-pin screw terminals ([AliExpress](https://www.aliexpress.com/item/32919824190.html))

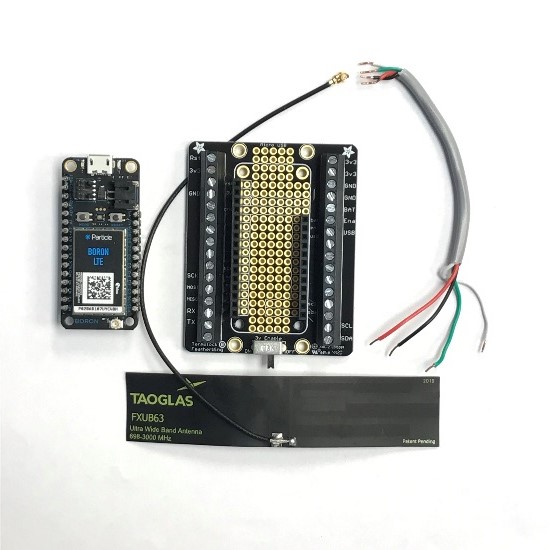
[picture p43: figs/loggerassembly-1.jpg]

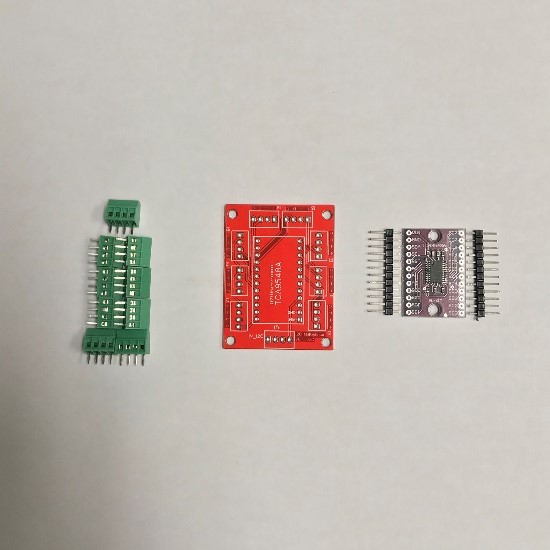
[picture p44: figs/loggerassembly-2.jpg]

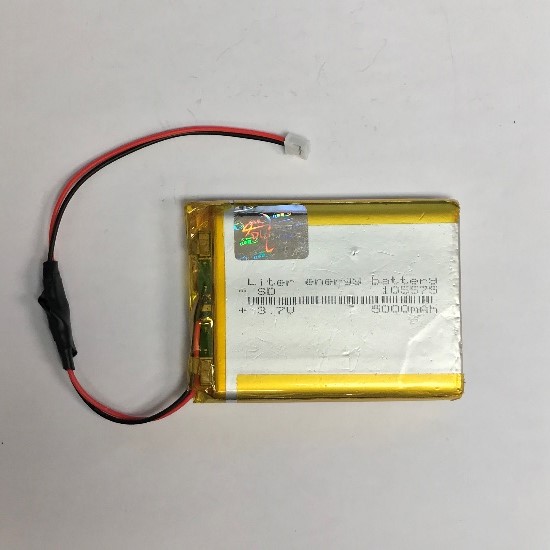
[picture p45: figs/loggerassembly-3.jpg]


## Assembly

 **Please note that if you only need one or two SHT-31 sensors attached to a data logger, the multiplexer is unnecessary. Simply attach the Boron to the Terminal block, and insert a battery** If you would like to add multiplexing capabilties, continue on.

- Order our custom, open source printed circuit board (PCB) which houses a multiplexer breakout board with screw terminal blocks. Download the \*.gerber files for our custom PCB. You can upload these files to any PCB printer. We use JLCPCB.com. Be sure to adjust surface finish to LeadFree HASL-RoHs. See this [video tutorial on ordering PCBs](https://www.youtube.com/watch?v=8r9syPCoZEs)



Donwload and print custom PCB using the [Custom PCB \*.gerber](../files/Custom_PCB_gerber.zip) files.

- Insert the male header pins for TCA9548A into the custom PCB board. Solder all male header pins to the TCA9548A Multiplexer.

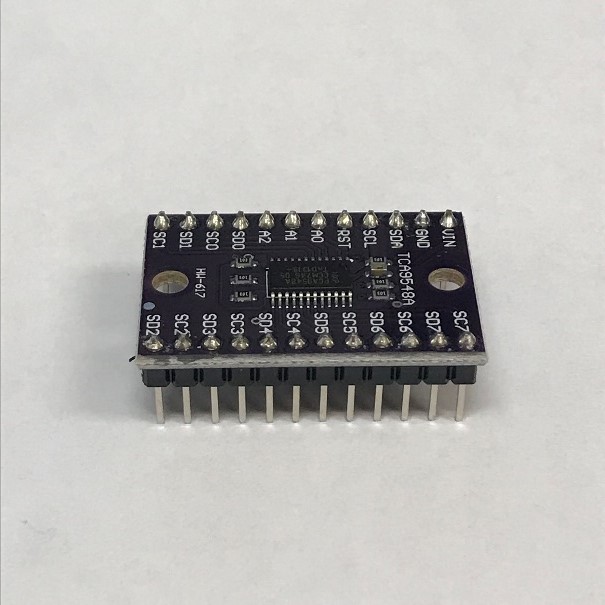
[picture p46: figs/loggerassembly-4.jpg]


- Insert a 4-pin screw terminal into each designated slot in the PCB board, and then solder each one. Make sure to apply a little extra solder to these in order to reinforce them for repeated use.


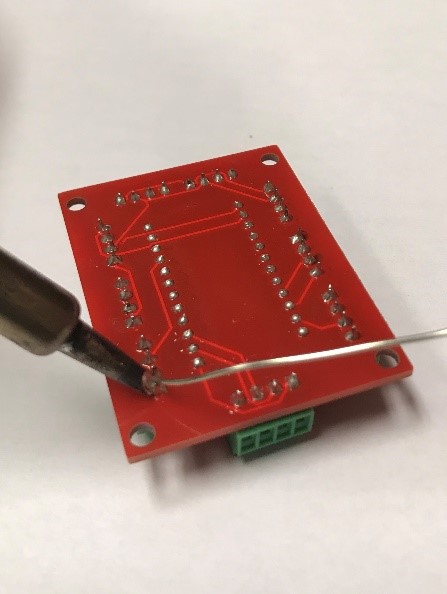
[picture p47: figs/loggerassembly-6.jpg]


- Attach the antenna to the Particle Boron, and then dock the Particle Boron in the associated female header pins located on the Breakout board.
 
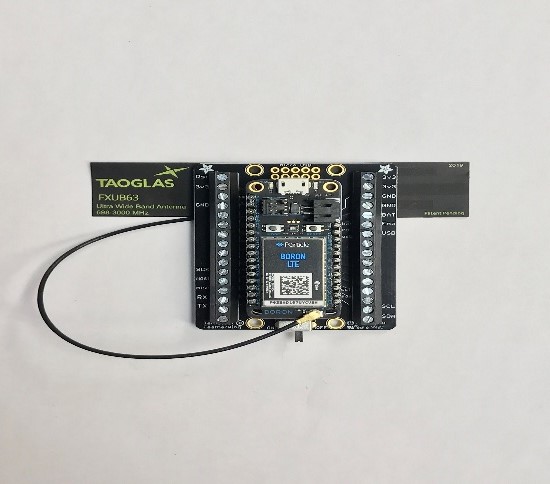
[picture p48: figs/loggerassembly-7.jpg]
 
 
 - Strip the shielded cable on each end (~3-4cm on one end and 1-2cm on the other) and place the wires on the longer end in their respective places on the screw terminals of the Breakout board, which are: Red = 3v3; Black = GND; White = SCL; Green = SDA. Attach the assembled TCA9548A module to the Particle module with the short end of the cable, with wiring as: Red = VIN; Black = GND; Green = SDA; White = SCL.

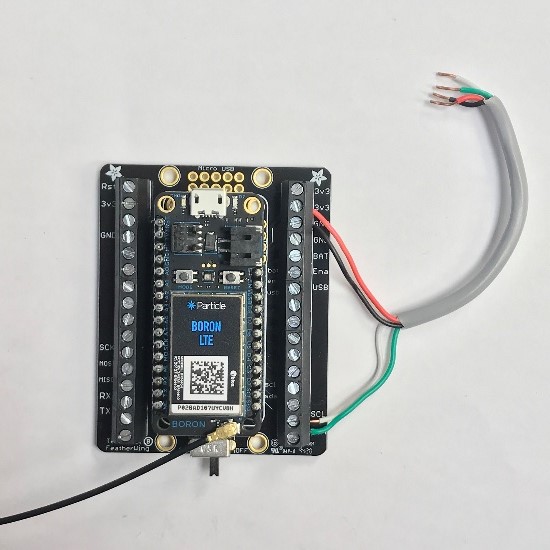
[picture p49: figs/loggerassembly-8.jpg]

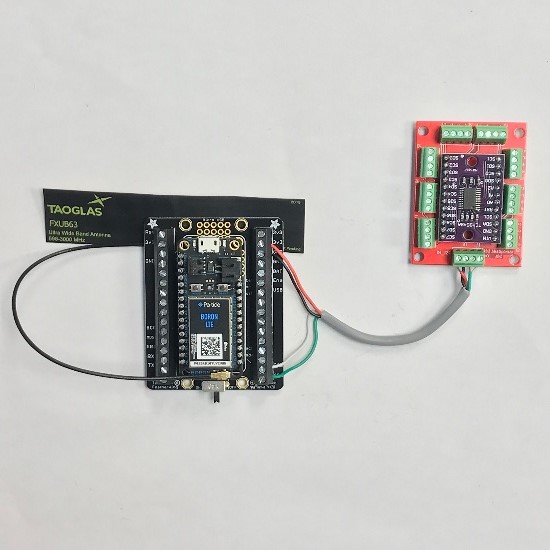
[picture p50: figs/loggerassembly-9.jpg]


- Plug the 3.7V battery into the Particle Boron using the 2-pin female plug, and arrange the completed components as shown for the most compact configuration (can be zip-tied to ensure they stay together but you may want to wait until all sensors are attached to allow access to ports).



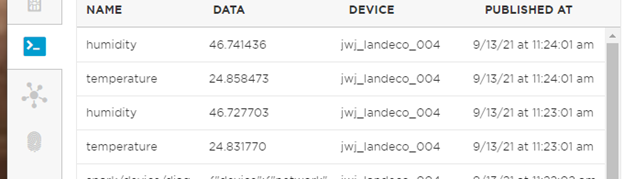
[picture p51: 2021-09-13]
figs/setup-capture3.png

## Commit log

2021-04-27 Create SHT-assembly
2021-09-13 moving stl files
    [Zip_Tie_Box.stl, Zip_Tie_Lid.stl]
